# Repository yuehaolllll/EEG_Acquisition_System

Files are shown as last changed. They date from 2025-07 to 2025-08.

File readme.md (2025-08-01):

# 1、EEG Acquisition System Description
*本EEG信号采集系统采用STM32F405RGT6作为主控，模数转换芯片采用TI的具有高精度8通道的ADS1299，另外结合WiFi模块用于传输数据。本系统采用外部±2.5V参考电压，最多支持24通道，采用级联法：共用SPI接口，3个CS片选引脚。*  
*MOSI：PB15 (SPI2)*  
*MISO：PB14 (SPI2)*  
*SCLK：PB13 (SPI2)*  
*CS1：  PB 12*  
*DRDY：PC6*  
*START：PC7*  
*RESET：PC8*  
*（级联另外两片）：*  
*CS2：PA12*  
*CS3：PA11*  

*文件ads1299v3.2为前端信号采集驱动代码，不同的采集模式主要通过配置寄存器来实现。主要配置方法参考如下：*  
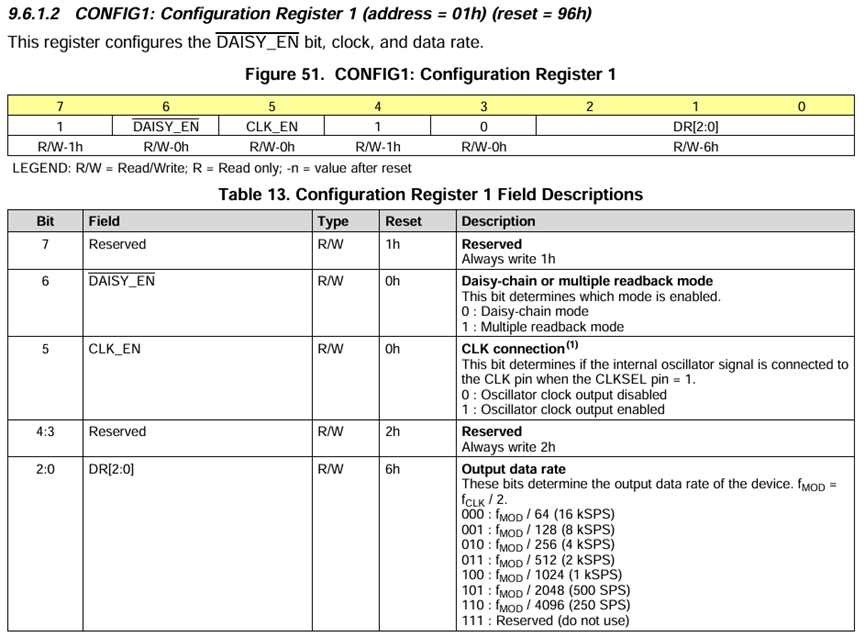
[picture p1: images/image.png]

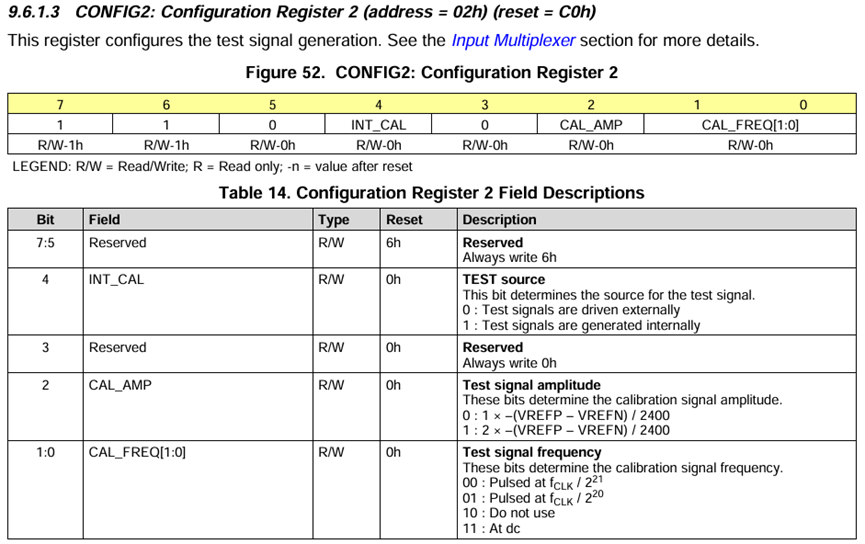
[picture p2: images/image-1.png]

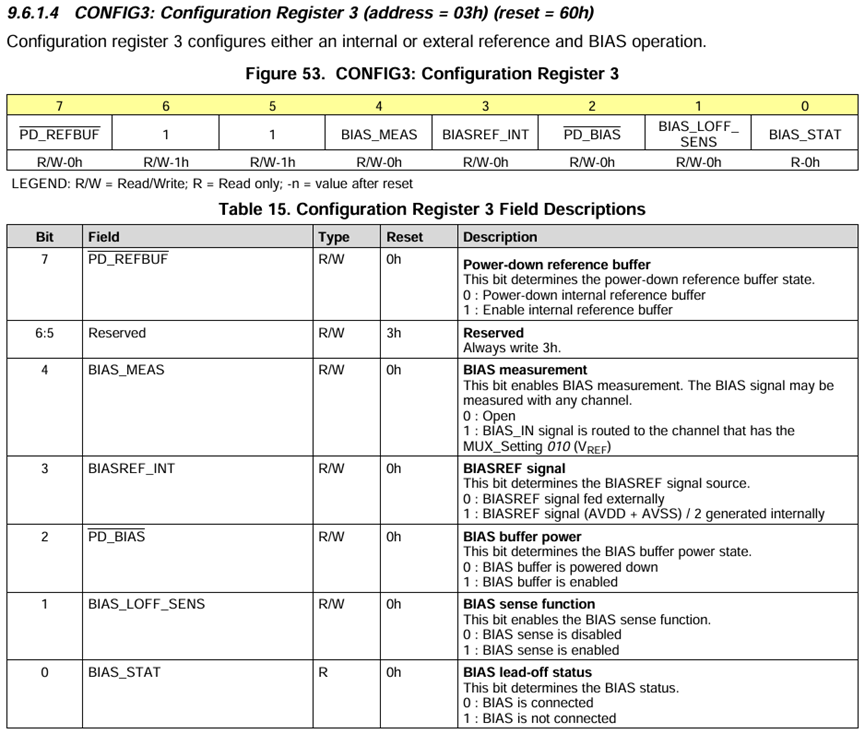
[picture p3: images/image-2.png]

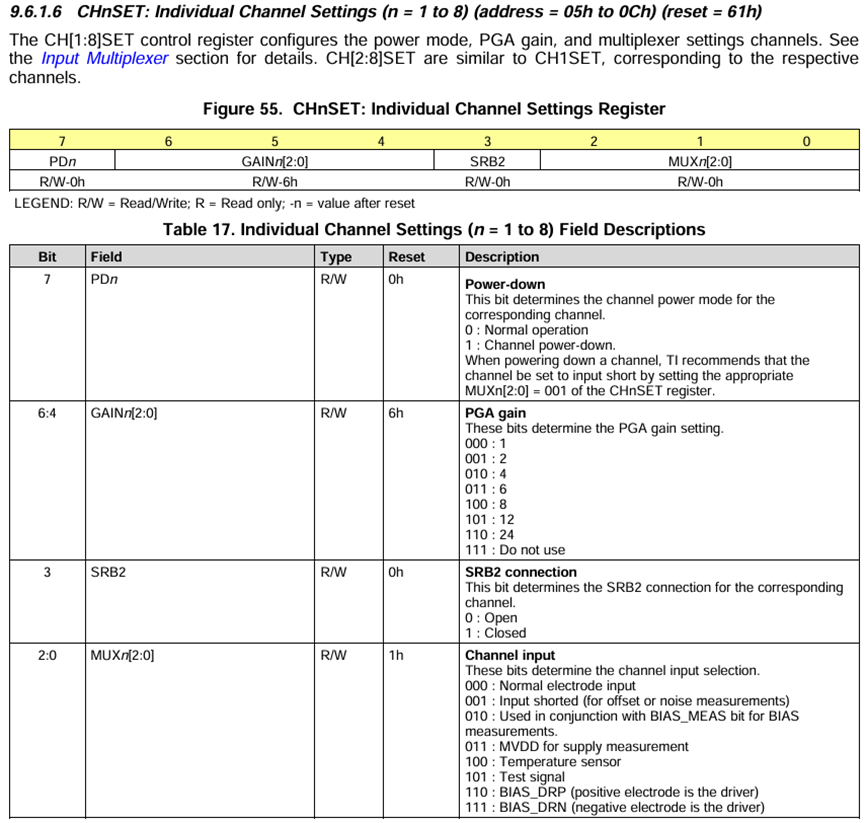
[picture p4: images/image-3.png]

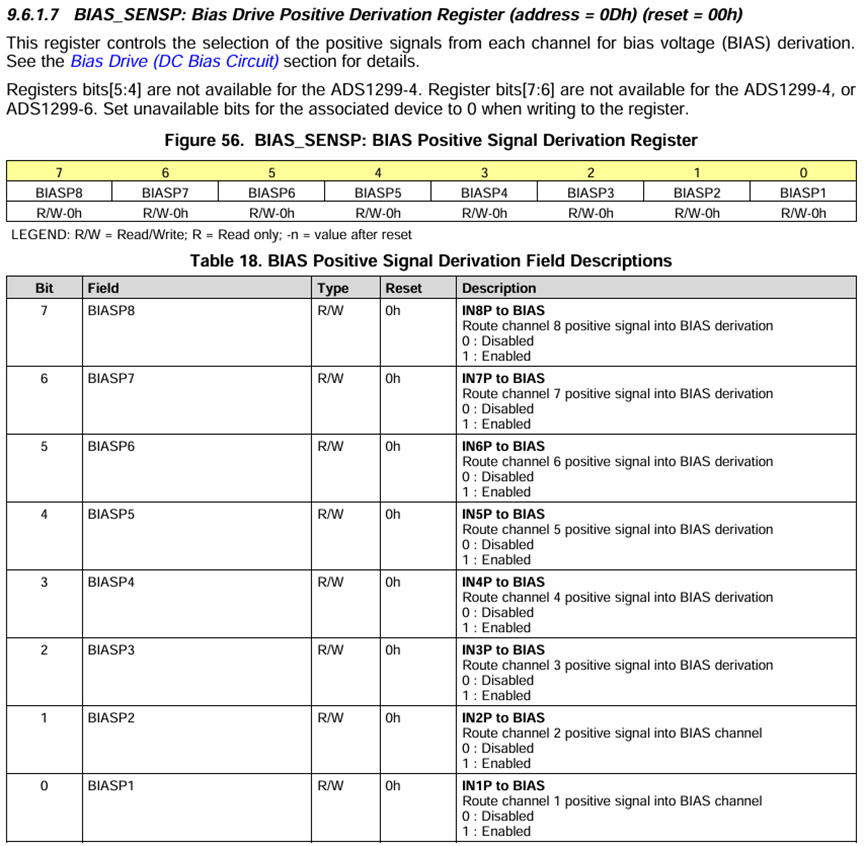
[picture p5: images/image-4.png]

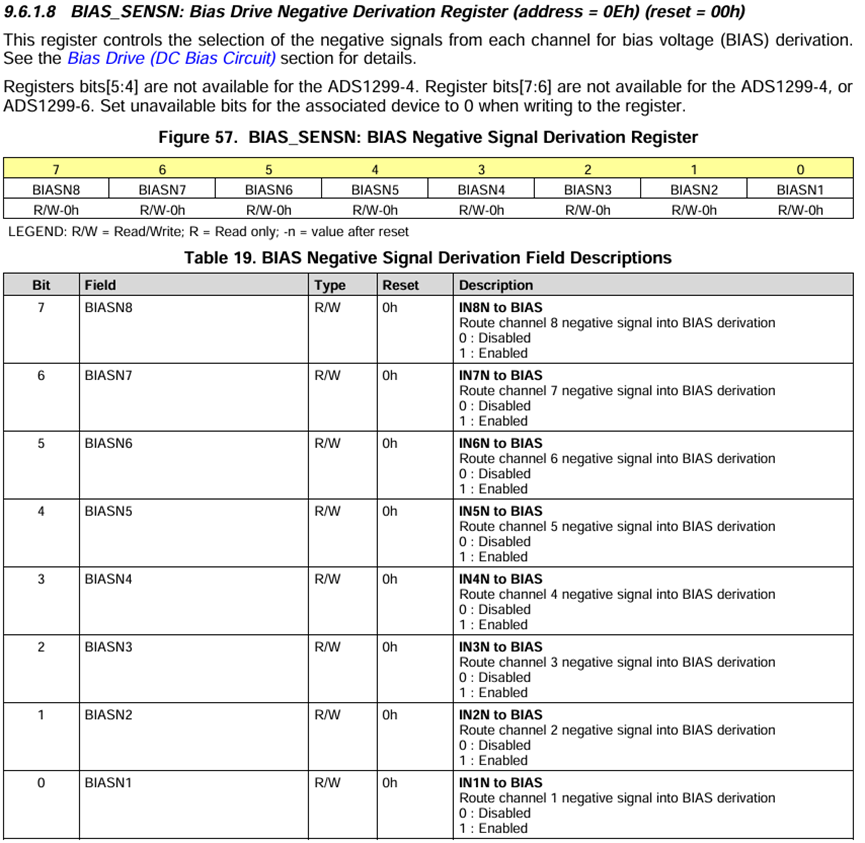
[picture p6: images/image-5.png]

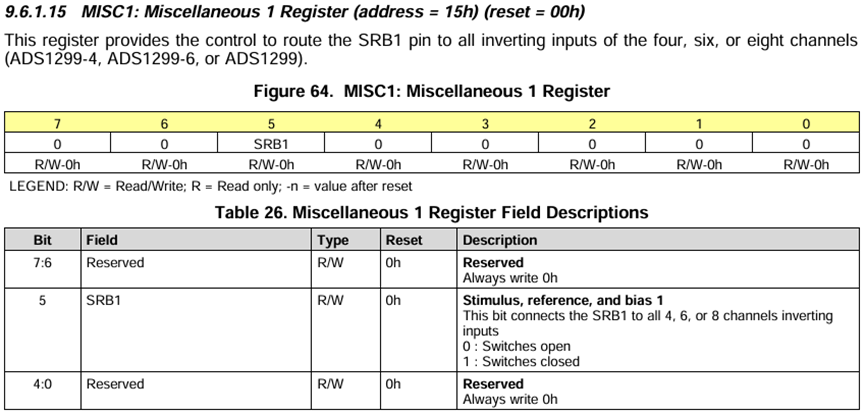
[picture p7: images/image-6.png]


*采集信号采用单端模式，即对于关注信号只需要连接正电极即可，需要配置所有的IN×N引脚共同连接到SRB1用于给系统提供稳定的零点为参考点。对于脑电信号，通常用右耳垂作为参考电极（REF），对于心电信号，则是右大腿。此外，还需连接偏置/驱动电极来抑制共模干扰，通常连接至受试者的腿部。*  
*文件eeg_realtime_plot_v2.0.py则是接收前端采集信号的python脚本代码，其中的配置需结合前端采集模式进行灵活修改。该代码实现实时的信号接收、压值转换、滤波（高通滤波、陷波滤波与滑动窗口滤波）、保存与绘制。*  
#  2、System Performance Evaluation
###  internal test signal
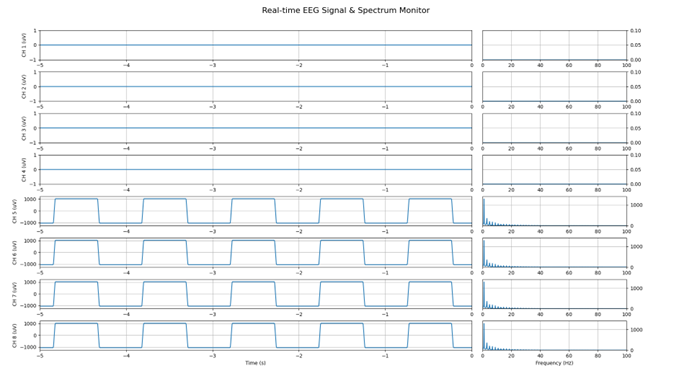
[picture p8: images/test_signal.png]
  
*从这张图片可以看出内部测试信号可以完美的采集到，并且噪音小，幅度吻合*  
###  shorted input to get background noise
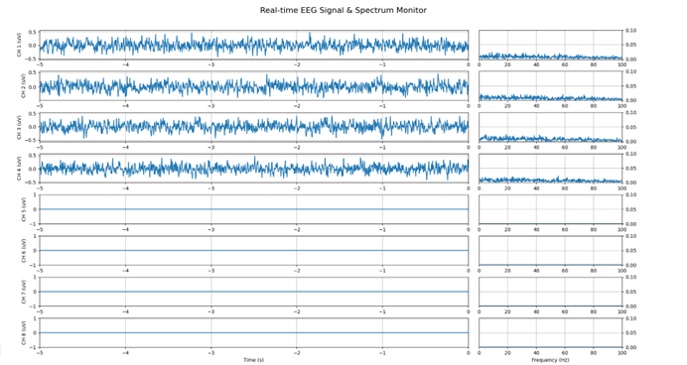
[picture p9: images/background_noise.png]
  
*根据参考手册的提示，在输入短路模式下所采集到的信号为系统的本底噪声。在增益为24，±2.5V参考电压的背景下，系统的本底噪声处于1uV的范围内，性能还算可以*  
###  ECG Test
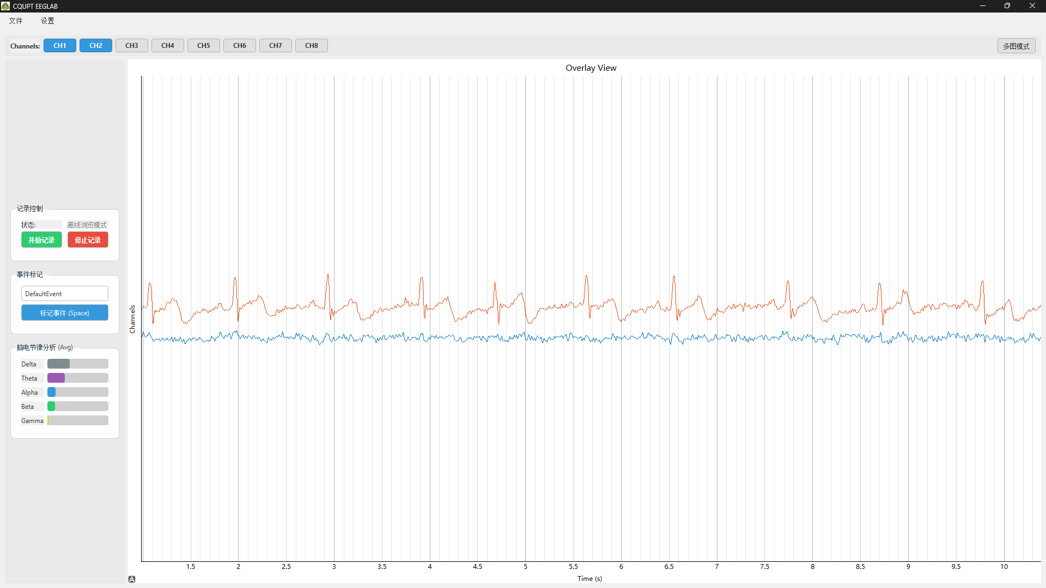
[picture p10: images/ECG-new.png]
  
*如图所示的通道一为采集到的心电信号波形图。心电信号主要由P波（心房收缩）、QRS波群（心室收缩）和T波（心室舒张）组成，幅度范围为-0.5mV到+2.0mV之间。经验证该信通可以采集较为精确心电信号*  
### EMG Test
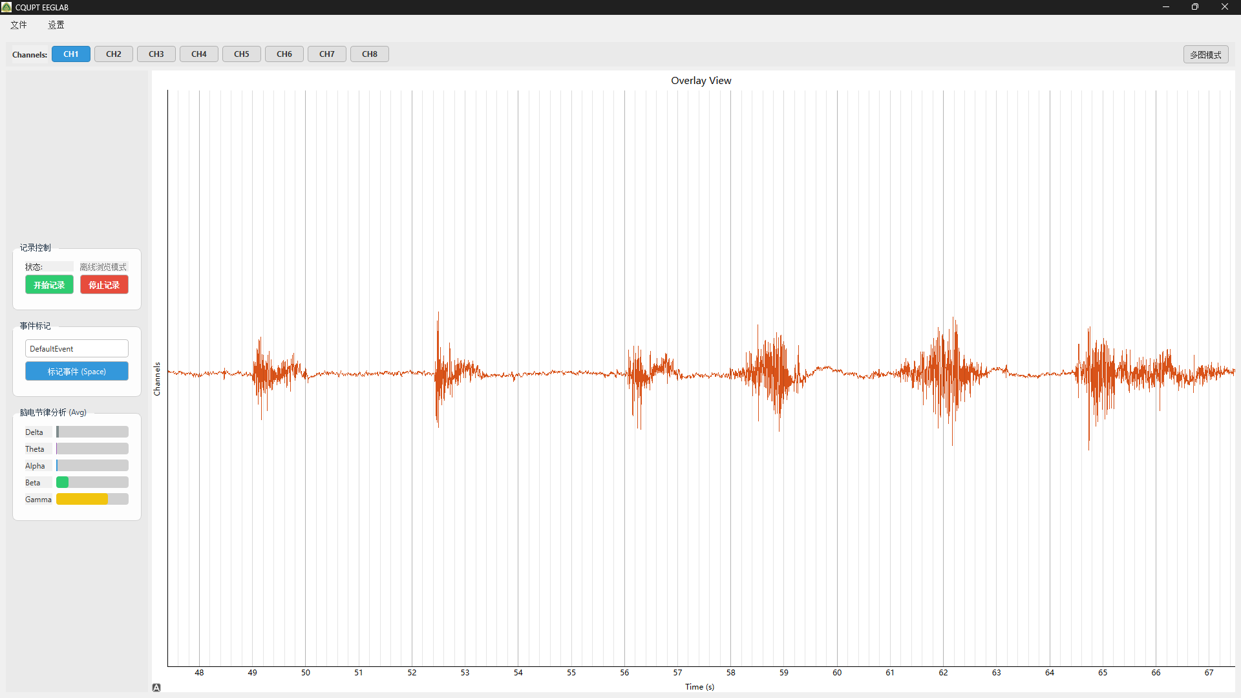
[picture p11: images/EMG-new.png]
 
*如图所示的通道一为采集到的肌电信号波形图。该图反映整个系统可以准确采集肌电信号，观察右侧的频率波形，也能体现出典型的肌电信号频域特征*  
### EOG Test
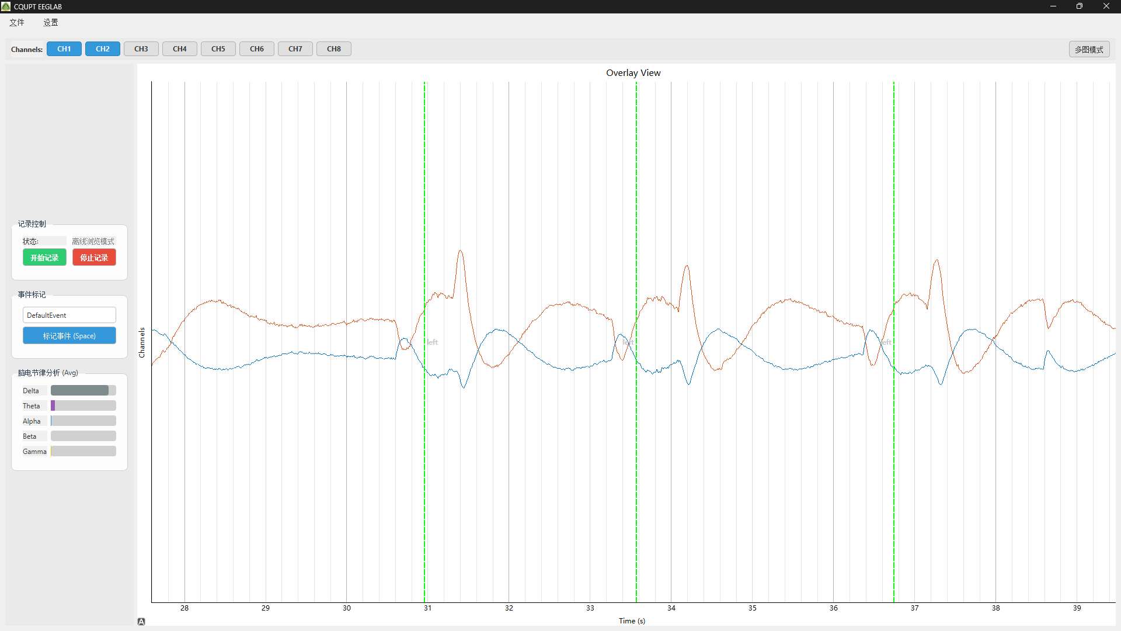
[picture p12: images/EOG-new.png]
  
*如图所示的通道一为采集到的眼动伪影波形图。图中可以看出眼动信号可以被准确采集*  
### EEG Test
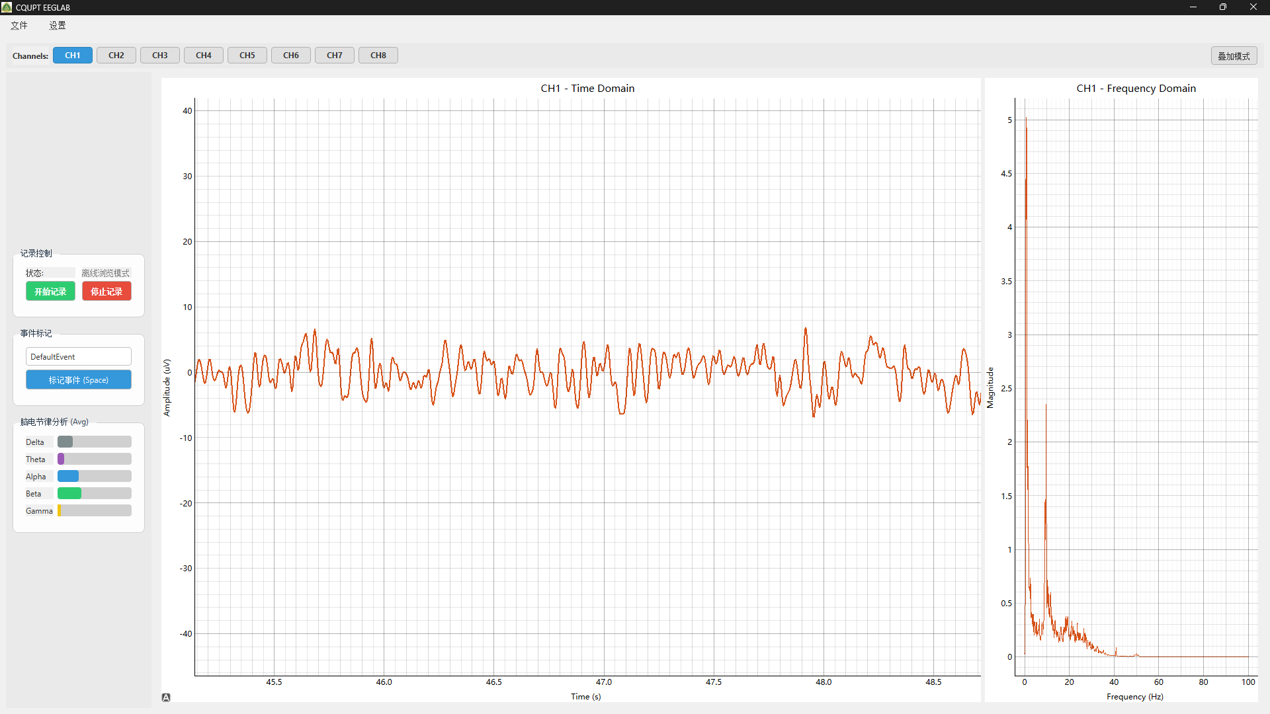
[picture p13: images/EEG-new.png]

*如图所示的通道一为采集到的脑电信号波形图。此图中可以清晰看到10Hz频率附近幅度明显，这就是Alpha波。*

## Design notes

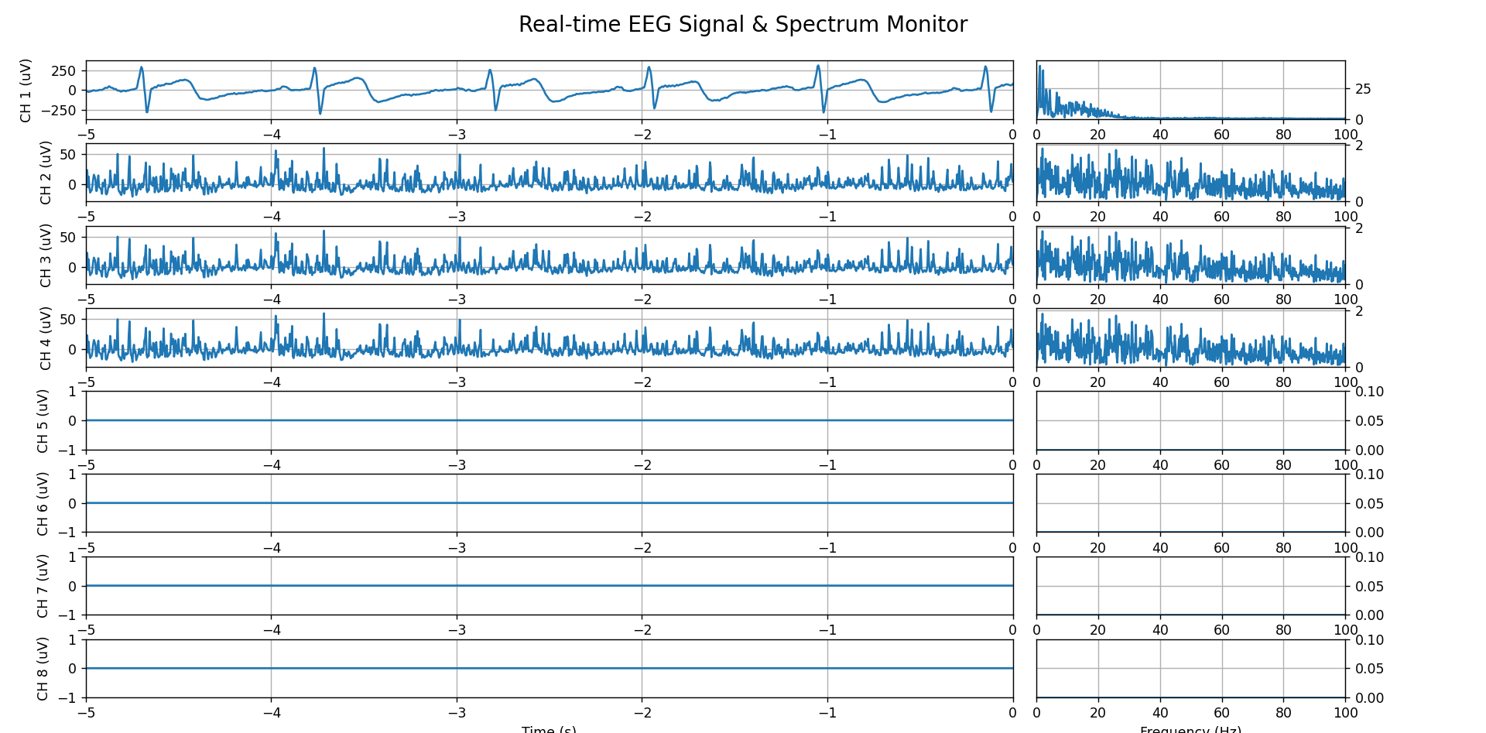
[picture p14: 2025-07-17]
images/ECG.png

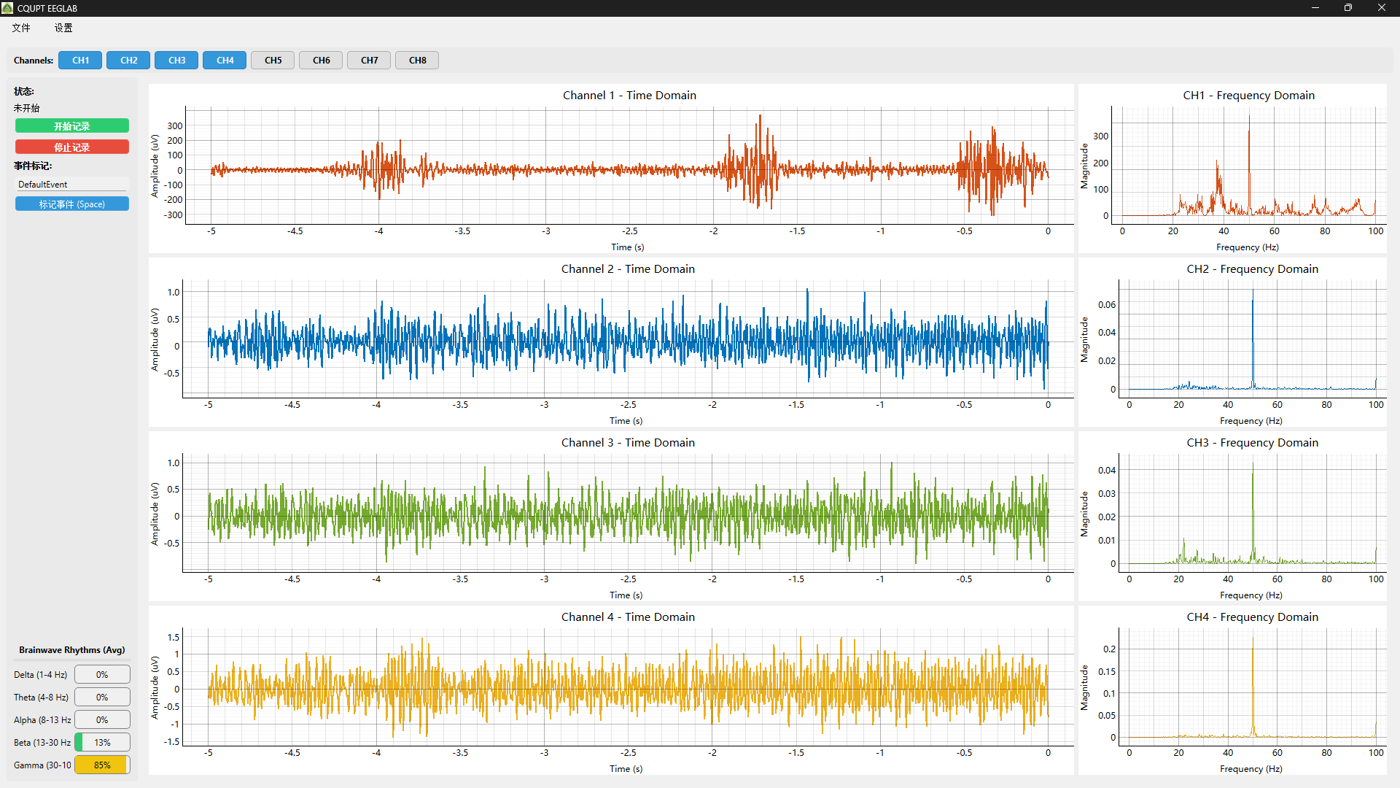
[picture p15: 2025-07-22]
images/EMG.png

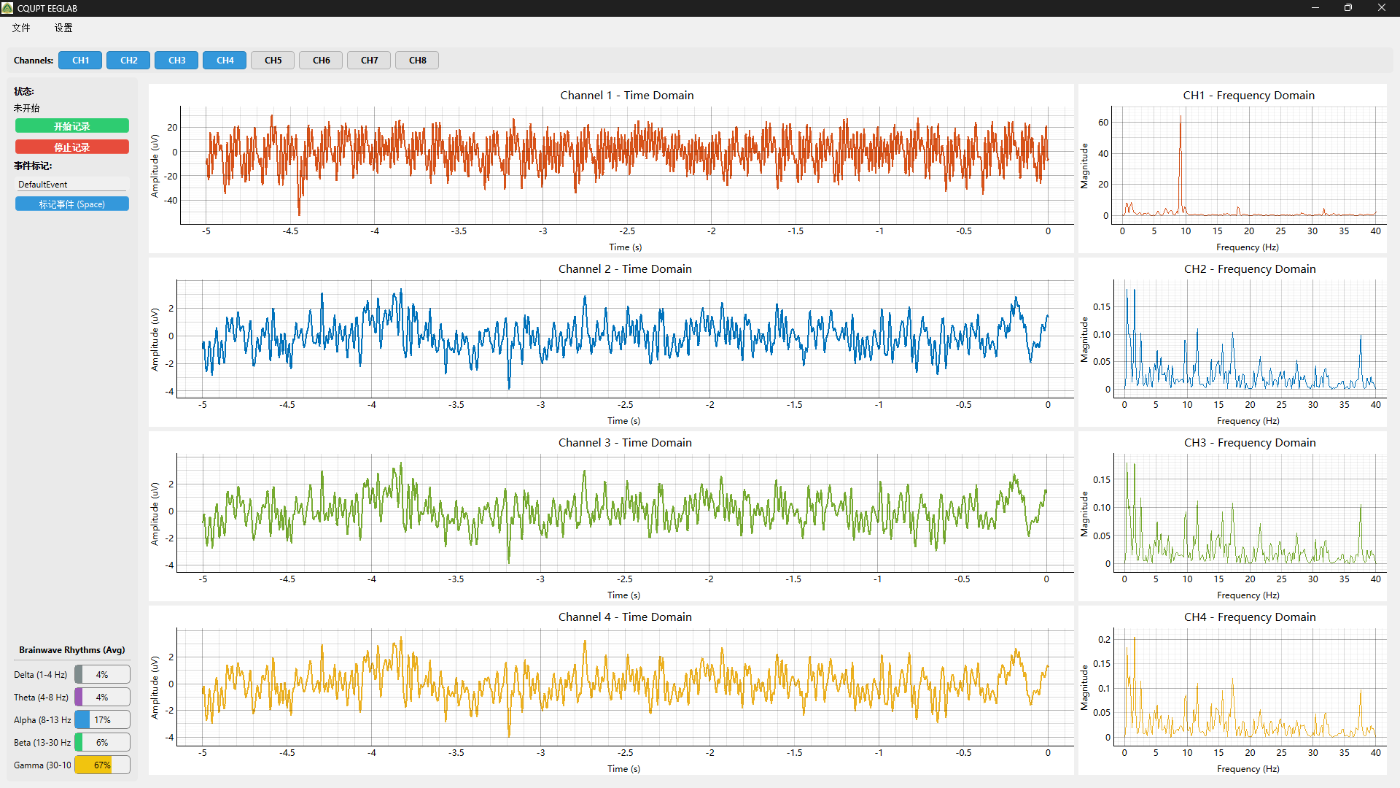
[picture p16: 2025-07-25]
images/Alpha_wave.png

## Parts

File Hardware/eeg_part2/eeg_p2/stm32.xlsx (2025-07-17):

Comment | Description | Designator | Footprint | LibRef | Quantity | jlc_id
100nF | 贴片电容/MLCC电容 | C1, C12, C13, C17, C18, C21, C22, C25, C26, C28, C29, C30, C31, C32, C34, C36 | C0603_L | C | 16
100nf | 贴片电容/MLCC电容 | C2, C3, C4, C5, C6, C7 | C0402_L | C | 6
18pf | 贴片电容/MLCC电容 | C8, C9 | C0402_L | C | 2
2.2uf | 贴片电容/MLCC电容 | C10, C11 | C0402_L | C | 2
4.7uF | 贴片电容/MLCC电容 | C14, C15 | C0603_M | C | 2
100uf/6.3V | 贴片电容/MLCC电容 | C16, C23, C24 | C1206_L | C | 3 | C45783, C15008
22uf/25v | 贴片电容/MLCC电容 | C19, C20 | C0805_L | C | 2 | C45783
22uf/25V | 贴片电容/MLCC电容 | C27 | C1206_L | C | 1
10uf | 贴片电容/MLCC电容 | C33, C35 | C0603_L | C | 2
3.5*1.3 | 低压DC电源接口 | CON1 | DC-005 | DC002~DC005 | 1
UDD32C03L01 | TVS通用 C78439, 静电和浪涌保护 3.3V双向 | D1, D2, D4 | SOD-323 | TVS, UDD32C03L01 | 3 | [NoParam], C78439
B340A-13-F | 肖特基二极管 C85098 | D3 | SMA | B340A-13-F | 1
10uF/10V | 贴片钽电容 C7171 | E1, E3 | C_3216 | CT | 2
22uF/10V | 贴片钽电容 C11366 | E2, E4 | C_3216 | CT | 2
HDR-1X4 | 4P接插件 | JP1 | XH2.54-WI-4P | Header 4 | 1
HDR-1X2 | 2P接插件 | JP2 | PH2.0-L-2P | Header 2 | 1
HDR-1X3 | 3P接插件 | JP4 | HDR2.54-LI-3P | Header 3 | 1
HDR-1X4 | 4P接插件 | JP5, JP7 | HDR2.54-M-LI-4P | Header 4 | 2
HDR-1X12 | 12P接插件 | JP6 | HDR2.54-M-LI-12P | Header 12 | 1
4.7uH | CD系列贴片线绕功率电感 | L1, L2 | CD53 | L-SMD | 2 | C177246
红色 | 贴片LED | LED1, LED2, LED3 | LED0603_Y | LED | 3
绿色 | 贴片LED | LED4 | LED0603_Y | LED | 1
1K | 贴片电阻 | R1, R2, R7, R8 | R0603_L | R | 4
10K | 贴片电阻 | R3, R13, R14, R18, R19 | R0603_L | R | 5
0.05R | 贴片电阻 | R4 | R0805_M | R | 1 | C127691
0.1R | 贴片电阻 | R5 | R0805_M | R | 1 | C25334
471K | 热敏电阻 | R6 | PK0406 | RT | 1
110K | 贴片电阻 | R9 | R0603_L | R | 1
10K/0.1% | 贴片电阻 | R10, R12 | R0603_L | R | 2
15K | 贴片电阻 | R11 | R0603_L | R | 1
4.7K | 贴片电阻 | R15, R16 | R0402_L | R | 2
10K | 贴片电阻 | R17 | R0402_L | R | 1
33K | 贴片电阻 | R20 | R0402_L | R | 1
BSMD1206-100-24V | PPTC自恢复保险丝 C910830 | RF1, RF2 | F1206 | FUSE-PPTC | 2 | C910830, [NoParam]
BSMD1812-100-24V | PPTC自恢复保险丝 C910830 | RF3 | F1812 | FUSE-PPTC | 1 | C883154
SS-12F23 | 1路波动开关 | S1 | SS-12D10 | SSW-1P | 1
3*4*2.5 | 贴片4脚轻触开关 | SW1, SW2, SW3, SW4, SW5, SW6 | SW-SMD-4.2x3.2_4P | SW SMD-3*4*2.5 | 6
STM32F405RGT6 | ARM Cortex-M4 32b MCU+FPU, 210DMIP, 1024 kB Flash, 192+4 kB RAM, 51 I/Os, 64-pin LQFP, -40 to +85癈, Tray | U1 | TQFP64_V | STM32F405RGT6 | 1
SLM6305 | 1锂电池充电ic 2.5a 4.2v 4V~26V输入 | U2 | DFN10-L3.0-W3.0-P0.5_EP | SLM6305 | 1 | C711584
LM358_NSC | Fast Settling Dual Operational Amplifier | U3 | SOP8_N | LM358_NSC | 1 | C2923376
MT3608L | Boost升压DC-DC芯片 2-28V | U4 | SOT23-6M | MT3608L | 1
CH340N | USB转串口芯片, 内置晶振 | U5 | SOIC-8 | CH340N | 1
Ai-WB2-12F | esp32-12f的替代 2.4g wifi和蓝牙 | U6 | ai-wb-12f | Ai-WB2-12F | 1
TYPE-C 2.0 -16P | USB2.0_Type-C_16Pin母座 C2765186 | USBC1 | USB-C-SMD_16P | USB2.0_Type-C_16Pin | 1
AMS1117-3V3 | 三端稳压芯片 | V1, V2 | SOT223_L | AMS1117 | 2
25MHZ | 4脚无源晶振(谐振器）C9006 | X1 | XTAL-3225-4P | XTAL-4P | 1 | C9006

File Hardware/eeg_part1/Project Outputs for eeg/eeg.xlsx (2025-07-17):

Comment | Description | Designator | Footprint | LibRef | Quantity | jlc_id
10nF | 贴片电容/MLCC电容 | C1, C11, C21, C31, C79, C87 | C0603_L | C | 6
100nF | 贴片电容/MLCC电容 | C2, C3, C7, C8, C10, C12, C13, C17, C18, C20, C22, C23, C27, C28, C30, C32, C33, C37, C38, C40, C41, C44, C53, C61, C66, C70, C73, C74 | C0603_L | C | 28
10uF | 贴片电容/MLCC电容 | C4, C6, C14, C16, C24, C26, C34, C36, C60, C68, C69, C71, C77, C78, C84, C85 | C0603_L | C | 16
4.7uF | 贴片电容/MLCC电容 | C5, C15, C25, C35 | C0603_L | C | 4
1nF | 贴片电容/MLCC电容 | C9, C19, C29, C39 | C0603_L | C | 4
4.7nF | 贴片电容/MLCC电容 | C42, C43, C45, C46, C47, C48, C50, C51 | C0603_L | C | 8
1.5nF | 贴片电容/MLCC电容 | C49, C52 | C0603_L | C | 2
1uF | 贴片电容/MLCC电容 | C54, C55, C56, C57, C58, C59, C62, C64, C67, C72, C80, C81, C82 | C0603_L | C | 13
100uF | 贴片电容/MLCC电容 | C63 | C1206_L | C | 1 | C7432784
150nF | 贴片电容/MLCC电容 | C65 | C0603_L | C | 1
2.2uF | 贴片电容/MLCC电容 | C75, C76, C83, C86 | C0603_L | C | 4
ADA4522-2ARZ | 双通道55V、EMI增强型、零漂移、超低噪声、RRO运算放大器 | IC1, IC2, IC3, IC4, IC5 | SOIC-8 | ADA4522-2ARZ | 5 | C403697
Header2X2 | 2*2P接插件 | JP1 | HDR2.54-WI-2x2P | Header 2X2 | 1
Header 4X2 | 4*2P接插件 | JP2, JP3 | HDR2.54-WI-2x4P | Header 4X2 | 2
HDR-1X10 | 10P接插件 | JP4 | HDR2.54-LI-10P | Header 10 | 1
3.3uH | 贴片小功率电感 | L1, L2 | L0805 | L | 2 | C162585
2M | 贴片电阻 | R1, R11, R21, R31 | R0603_L | R | 4
5.49K 0,01% | 贴片电阻 | R2, R3, R12, R13, R22, R23, R32, R33 | R0603_M | R | 8
0R | 贴片电阻 | R4, R5, R14, R15, R24, R25, R34, R35, R42, R47, R63, R65 | R0603_L | R | 12
20K 1% | 贴片电阻 | R6, R16, R26, R36 | R0603_L | R | 4
10K 1% | 贴片电阻 | R7, R8, R17, R18, R27, R28, R37, R38 | R0603_L | R | 8
330K 1% | 贴片电阻 | R9, R19, R29, R39 | R0603_L | R | 4
470K 1% | 贴片电阻 | R10, R20, R30, R40 | R0603_L | R | 4
5.1K | 贴片电阻 | R41, R43, R44, R45, R52, R54, R55, R56 | R0603_L | R | 8
100K | 贴片电阻 | R46, R57, R60, R61, R62, R64 | R0603_L | R | 6
0R_N | 贴片电阻 | R48, R49, R50, R51, R58, R66 | R0603_L | R | 6
1MR | 贴片电阻 | R53 | R0603_L | R | 1
1M | 贴片电阻 | R59 | R0603_L | R | 1
2K | 贴片电阻 | R67 | R0603_L | R | 1
1K | 贴片电阻 | R68 | R0603_L | R | 1
47 | 贴片电阻 | R69 | R0603_L | R | 1
20K 0.1% | 贴片电阻 | R70, R71 | R0603_L | R | 2
0R | 贴片电阻 | R72 | R1206_L | R | 1
INA333AIDGKR | INA333 低功耗、零漂移、精密仪表放大器 | U1, U2, U3, U4 | MSOP8_N | INA333AIDGKR | 4 | C19450
TPD4E1B06DCKR | 具有 0.5nA 最大泄漏电流的四路 0.7pF、±5.5V、±12kV ESD 保护二极管 | U5, U6, U7, U8, U9 | SOT363_N | TPD4E1B06DCKR | 5 | C840093
ADS1299IPAGR | 24位、多通道EEG/ECG ADC，内置增益放大 | U10 | TQFP64_N | ADS1299IPAGR | 1 | C476817
REF5025AIDR | 2.5V、3μVpp/V 噪声、3ppm/°C 温漂、精密串联电压基准 | U11 | SOIC-8 | REF5025AIDR | 1 | C544535
OPA388 | OPA388 单路、10MHz、CMOS、零温漂、零交叉、真 RRIO 精密运算放大器 | U12, U13 | SOIC-8 | OPA388 | 2 | C11341
TPS73225DBVR | 2.5V输出LDO 30uVRMS 精度1% | U14 | SOT23-5 | TPS73225DBVR | 1
TPS60403DBVR | 60mA 充电泵电压反向器 250khz | U15 | SOT23-5 | TPS60403DBVR | 1
TPS72325DBVT | 200mA 负输出低压降线性稳压器 5-SOT-23 -40 to 125 | U16 | SOT23-5 | TPS72325DBVT | 1 | C2864241

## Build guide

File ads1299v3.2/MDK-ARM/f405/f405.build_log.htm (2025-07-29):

µVision Build Log

Tool Versions:

IDE-Version: ¦ÌVision V5.34.0.0
Copyright (C) 2021 ARM Ltd and ARM Germany GmbH. All rights reserved.
License Information: yue pcc, proud, LIC=LSNXV-P1EDA-FW52N-YE3SL-EXBRL-V5UCF
 
Tool Versions:
Toolchain:       MDK-ARM Plus  Version: 5.34.0.0
Toolchain Path:  F:\Keil\ARM\ARMCC\Bin
C Compiler:      Armcc.exe V5.06 update 7 (build 960)
Assembler:       Armasm.exe V5.06 update 7 (build 960)
Linker/Locator:  ArmLink.exe V5.06 update 7 (build 960)
Library Manager: ArmAr.exe V5.06 update 7 (build 960)
Hex Converter:   FromElf.exe V5.06 update 7 (build 960)
CPU DLL:         SARMCM3.DLL V5.34.0.0
Dialog DLL:      DCM.DLL V1.17.3.0
Target DLL:      STLink\ST-LINKIII-KEIL_SWO.dll V3.0.8.0
Dialog DLL:      TCM.DLL V1.48.0.0

Project:

F:\EEG\TeamEEG\EEG_Acquisition_System\ads1299v3.2\MDK-ARM\f405.uvprojx
Project File Date:  07/10/2025

Output:

*** Using Compiler 'V5.06 update 7 (build 960)', folder: 'F:\Keil\ARM\ARMCC\Bin'
Build target 'f405'
compiling ads1299.c...
linking...
Program Size: Code=22348 RO-data=852 RW-data=176 ZI-data=18008  
FromELF: creating hex file...
"f405\f405.axf" - 0 Error(s), 0 Warning(s).

Software Packages used:

Package Vendor: ARM
                http://www.keil.com/pack/ARM.CMSIS.5.7.0.pack
                ARM.CMSIS.5.7.0
                CMSIS (Cortex Microcontroller Software Interface Standard)
   * Component: CORE Version: 5.4.0

Package Vendor: Keil
                https://www.keil.com/pack/Keil.STM32F4xx_DFP.3.0.0.pack
                Keil.STM32F4xx_DFP.3.0.0
                STMicroelectronics STM32F4 Series Device Support

Collection of Component include folders:

  .\RTE\_f405
  F:\Keil\ARM\CMSIS\5.7.0\CMSIS\Core\Include

Collection of Component Files used:

   * Component: ARM::CMSIS:CORE:5.4.0
      Include file:  CMSIS\Core\Include\tz_context.h
Build Time Elapsed:  00:00:03

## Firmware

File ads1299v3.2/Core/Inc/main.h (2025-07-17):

/* USER CODE BEGIN Header */
/**
  ******************************************************************************
  * @file           : main.h
  * @brief          : Header for main.c file.
  *                   This file contains the common defines of the application.
  ******************************************************************************
  * @attention
  *
  * Copyright (c) 2025 STMicroelectronics.
  * All rights reserved.
  *
  * This software is licensed under terms that can be found in the LICENSE file
  * in the root directory of this software component.
  * If no LICENSE file comes with this software, it is provided AS-IS.
  *
  ******************************************************************************
  */
/* USER CODE END Header */

/* Define to prevent recursive inclusion -------------------------------------*/
#ifndef __MAIN_H
#define __MAIN_H

#ifdef __cplusplus
extern "C" {
#endif

/* Includes ------------------------------------------------------------------*/
#include "stm32f4xx_hal.h"

/* Private includes ----------------------------------------------------------*/
/* USER CODE BEGIN Includes */

/* USER CODE END Includes */

/* Exported types ------------------------------------------------------------*/
/* USER CODE BEGIN ET */

/* USER CODE END ET */

/* Exported constants --------------------------------------------------------*/
/* USER CODE BEGIN EC */

/* USER CODE END EC */

/* Exported macro ------------------------------------------------------------*/
/* USER CODE BEGIN EM */

/* USER CODE END EM */

/* Exported functions prototypes ---------------------------------------------*/
void Error_Handler(void);

/* USER CODE BEGIN EFP */

/* USER CODE END EFP */

/* Private defines -----------------------------------------------------------*/
#define WIFI_EN_Pin GPIO_PIN_1
#define WIFI_EN_GPIO_Port GPIOB
#define CS_Pin GPIO_PIN_12
#define CS_GPIO_Port GPIOB
#define START_Pin GPIO_PIN_7
#define START_GPIO_Port GPIOC
#define RESET_Pin GPIO_PIN_8
#define RESET_GPIO_Port GPIOC
#define SPI3_CS2_Pin GPIO_PIN_11
#define SPI3_CS2_GPIO_Port GPIOA
#define SPI3_CS3_Pin GPIO_PIN_12
#define SPI3_CS3_GPIO_Port GPIOA
#define KEY1_Pin GPIO_PIN_10
#define KEY1_GPIO_Port GPIOC
#define KEY2_Pin GPIO_PIN_11
#define KEY2_GPIO_Port GPIOC
#define KEY3_Pin GPIO_PIN_12
#define KEY3_GPIO_Port GPIOC
#define KEY4_Pin GPIO_PIN_2
#define KEY4_GPIO_Port GPIOD
#define LED1_Pin GPIO_PIN_3
#define LED1_GPIO_Port GPIOB
#define LED2_Pin GPIO_PIN_4
#define LED2_GPIO_Port GPIOB

/* USER CODE BEGIN Private defines */

/* USER CODE END Private defines */

#ifdef __cplusplus
}
#endif

#endif /* __MAIN_H */

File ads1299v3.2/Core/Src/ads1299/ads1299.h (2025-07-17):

/* ads1299.h */
#ifndef __ADS1299_H__
#define __ADS1299_H__

#include "stm32f4xx_hal.h"
#include "cmsis_os.h"

// === SPI and GPIO Config ===
#define ADS1299_SPI               hspi2
#define ADS1299_CS_GPIO_Port      GPIOB
#define ADS1299_CS_Pin            GPIO_PIN_12
#define ADS1299_RESET_GPIO_Port   GPIOC
#define ADS1299_RESET_Pin         GPIO_PIN_8
#define ADS1299_START_GPIO_Port   GPIOC
#define ADS1299_START_Pin         GPIO_PIN_7
#define ADS1299_DRDY_GPIO_Port    GPIOC
#define ADS1299_DRDY_Pin          GPIO_PIN_6

extern SPI_HandleTypeDef ADS1299_SPI;

// === ADS1299 Commands ===
#define ADS1299_CMD_WAKEUP        0x02
#define ADS1299_CMD_STANDBY       0x04
#define ADS1299_CMD_RESET         0x06
#define ADS1299_CMD_START         0x08
#define ADS1299_CMD_STOP          0x0A
#define ADS1299_CMD_RDATAC        0x10
#define ADS1299_CMD_SDATAC        0x11
#define ADS1299_CMD_RDATA         0x12

#define ADS1299_CMD_RREG          0x20
#define ADS1299_CMD_WREG          0x40

// === ADS1299 Register Addresses ===
#define ADS1299_REG_ID            0x00
#define ADS1299_REG_CONFIG1       0x01
#define ADS1299_REG_CONFIG2       0x02
#define ADS1299_REG_CONFIG3       0x03
#define ADS1299_REG_LOFF          0x04
#define ADS1299_REG_CH1SET        0x05
#define ADS1299_REG_CH2SET        0x06
#define ADS1299_REG_CH3SET        0x07
#define ADS1299_REG_CH4SET        0x08
#define ADS1299_REG_CH5SET        0x09
#define ADS1299_REG_CH6SET        0x0A
#define ADS1299_REG_CH7SET        0x0B
#define ADS1299_REG_CH8SET        0x0C
#define ADS1299_REG_BIAS_SENSP    0x0D
#define ADS1299_REG_BIAS_SENSN    0x0E
#define ADS1299_REG_LOFF_SENS     0x0F
#define ADS1299_REG_CONFIG4       0x17
#define ADS1299_REG_MISC1         0x15

// === Structs ===
typedef struct  {
    uint8_t status[3];
    uint8_t channel_data[8][3];
} ADS1299_Data_t;

typedef struct {
    SPI_HandleTypeDef *hspi;
    osSemaphoreId dataReadySemaphore;
} ADS1299_Handle_t;


extern ADS1299_Handle_t adsHandle;
extern osSemaphoreId ads1299Semaphore;

// === API ===
void ADS1299_Init(ADS1299_Handle_t *dev);
void ADS1299_ReadData(ADS1299_Handle_t *dev, ADS1299_Data_t *data);
uint8_t ADS1299_ReadRegister(ADS1299_Handle_t *dev, uint8_t reg);
void ADS1299_WriteRegister(ADS1299_Handle_t *dev, uint8_t reg, uint8_t value);
//void ADS1299_Task(void const *argument);


#endif /* __ADS1299_H__ */

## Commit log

2025-07-17 EEG acquisition system v1.0
    [Pick Place for eeg.csv, ads1299.SchDoc, communication.SchDoc, eeg.GBL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]
2025-07-17 improvement framework
    [Pick Place for eeg.csv, ads1299.SchDoc, communication.SchDoc, eeg.GBL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]
2025-07-22 add lowpass filter
